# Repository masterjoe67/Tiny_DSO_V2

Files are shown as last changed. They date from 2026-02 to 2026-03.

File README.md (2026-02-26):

# Tiny_DSO_V2: 65MSPS Digital Storage Oscilloscope

Un oscilloscopio digitale ad alte prestazioni basato su architettura eterogenea **FPGA (Intel Cyclone IV)** e **Soft-Processor AVR**. Progettato per l'acquisizione di segnali in tempo reale con risoluzione a 12 bit.

<p align="center">
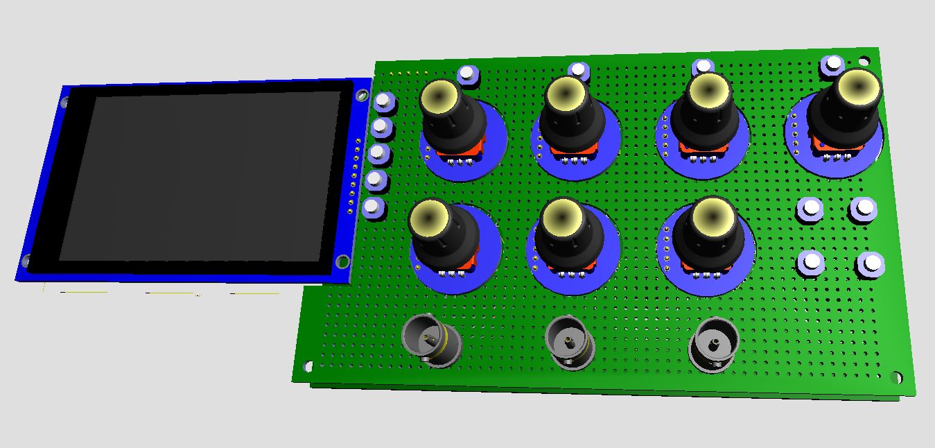
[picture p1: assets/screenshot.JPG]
Tiny DSO Preview
  
</p>

## 🚀 Caratteristiche Principali
- **Sampling Rate:** 65 MSPS (Real-time) tramite ADC parallelo.
- **Risoluzione:** 12 bit (AD9226).
- **Core CPU:** AVR V8 Soft-Core sintetizzato @ 60 MHz.
- **Trigger Engine:** Unità hardware dedicata con latenza di 15.4ns.
- **Display:** Supporto per controller ST7789 tramite SPI hardware ottimizzata.
- **Toolchain:** Compilato con l'ultima versione di AVR-GCC (15.1).

## 🛠️ Architettura del Sistema
Il progetto si divide in due componenti principali che lavorano in sinergia:

### 1. Hardware (VHDL/Verilog)
La logica programmabile gestisce le operazioni "time-critical":
- **ADC Controller:** Interfaccia parallela per l'AD9226 che cattura 12 bit per ciclo di clock.
- **Trigger System:** Monitoraggio continuo della soglia e gestione delle modalità `trigger_source`, `trigger_slope` e `trigger_mode`.
- **Memory Buffer:** Implementazione di buffer circolari in Block RAM per evitare la perdita di campioni durante la lettura della CPU.

### 2. Firmware (C)
Il software gestisce l'intelligenza dello strumento:
- **Rendering Differenziale:** Algoritmo ottimizzato per aggiornare solo i pixel necessari della traccia, riducendo il carico sul bus del display.
- **Interfaccia Utente:** Gestione degli input per la regolazione di scale temporali, offset e parametri di trigger.

## 📦 Requisiti di Sviluppo
- **FPGA:** Intel/Altera Cyclone IV (es. EP4CE22).
- **IDE:** Quartus Prime (per la sintesi hardware).
- **Toolchain:** AVR-GCC 15.1 o superiore (per il firmware).
- **Hardware ADC:** Modulo AD9226 (12-bit, 65MSPS).

---
*Developed by MJE 2026. Special thanks to M. Montanari (Perry) for the experimental PCB layout and wiring.*

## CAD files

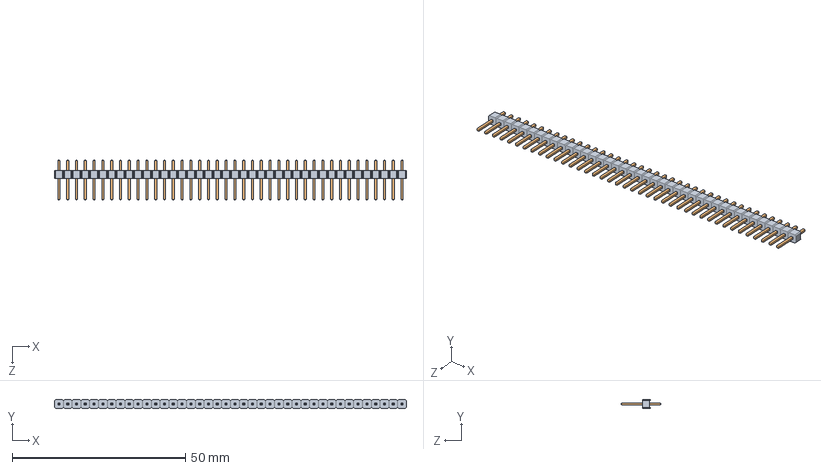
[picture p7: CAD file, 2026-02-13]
HARDWARE/CAD/User Library-Header_Male_40Pin/User Library-Header_Male_40Pin.sldasm
101.6 x 2.49 x 11.5 mm
User Library-Header_Male_40Pin_BodyArray
User Library-Header_Male_40Pin_PinArray

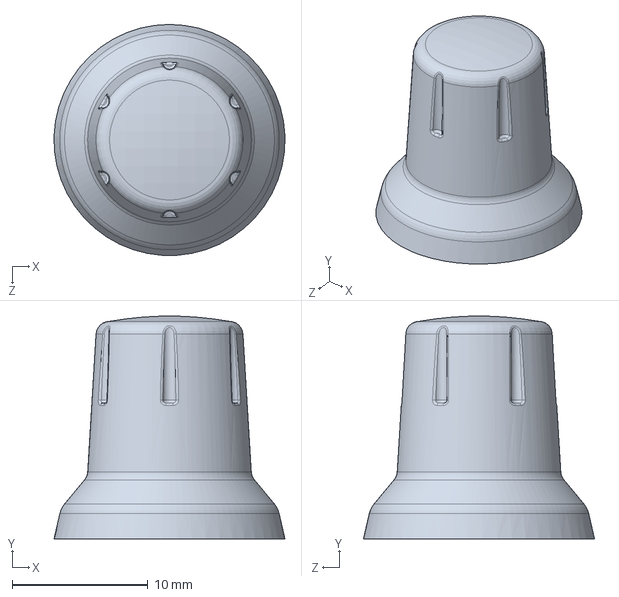
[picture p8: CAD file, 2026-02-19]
HARDWARE/CAD/Encoder/Manopola.SLDPRT
17.0 x 16.4 x 17.0 mm

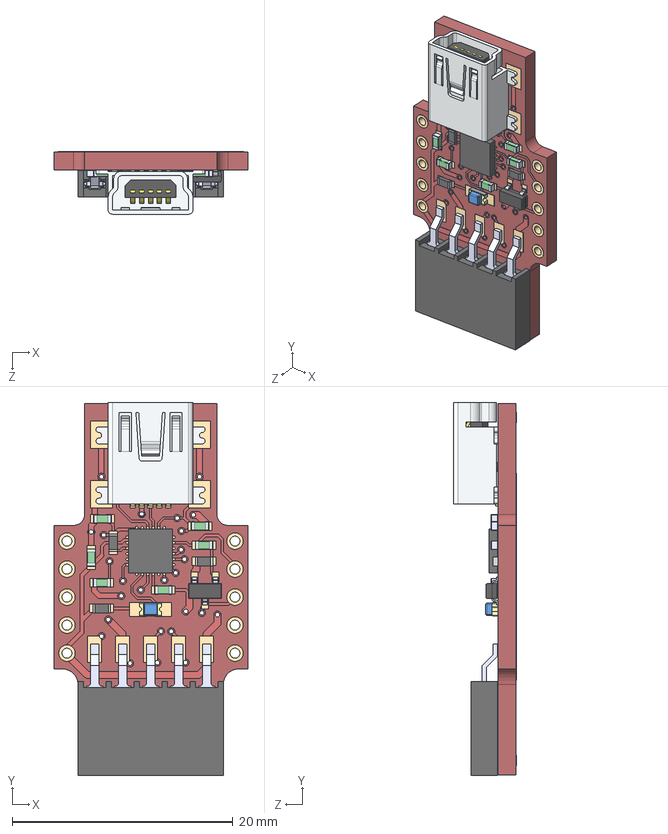
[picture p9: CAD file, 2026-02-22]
HARDWARE/CAD/uUSB-PA5-II.STEP
17.6 x 33.8 x 5.67 mm
uUSB-PA5-REV3.0aOutLine
Samtec-MUSB-05-S-B-SM-A^CN1_uUSB-PA5-REV3.0a-Components22
C-8-3_1st row (Default)^SMH-105-02-X-S_H1_uUSB-PA5-REV3.0a-Components22 x 5
ssw-xx-x_-S^SMH-105-02-X-S_H1_uUSB-PA5-REV3.0a-Components22
User Library-led_0805LED0805_blue^LED1_uUSB-PA5-REV3.0a-Components22
User Library-RES_0603L_RES_0603_Lead_1^User Library-RES_0603L x 6
User Library-RES_0603L_RES_0603_Body_1^User Library-RES_0603L x 3
User Library-cap_0603_lowprofile x 6
SW3DPS-SOT-23-DEFAULT^Q1_uUSB-PA5-REV3.0a-Components22
Extruded^9950061008_U1_uUSB-PA5-REV3.0a-Components22

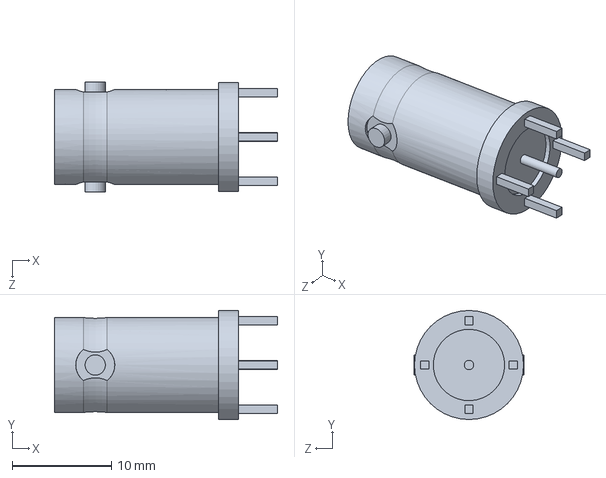
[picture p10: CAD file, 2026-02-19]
HARDWARE/CAD/BNC.SLDPRT
22.5 x 11.0 x 11.1 mm

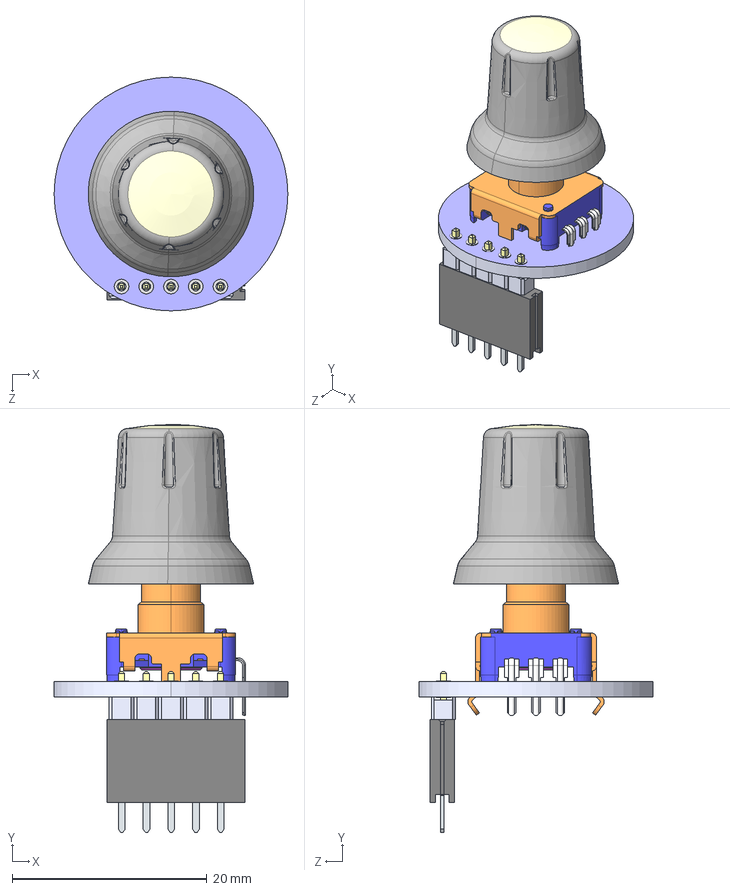
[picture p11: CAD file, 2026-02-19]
HARDWARE/CAD/Encoder/ENCODER_MODULE.STEP
24.0 x 41.9 x 24.0 mm

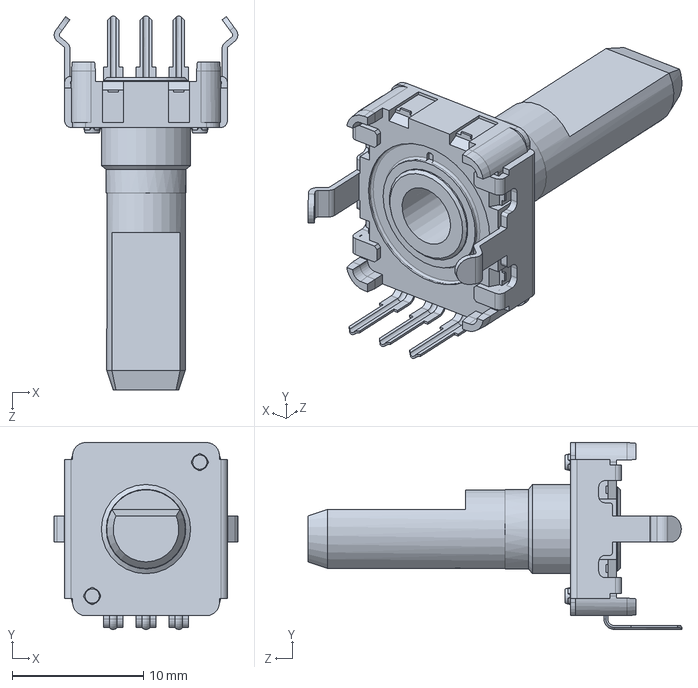
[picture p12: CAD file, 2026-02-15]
HARDWARE/CAD/Encoder/ec12e24204a9.SLDPRT
14.0 x 14.2 x 28.5 mm

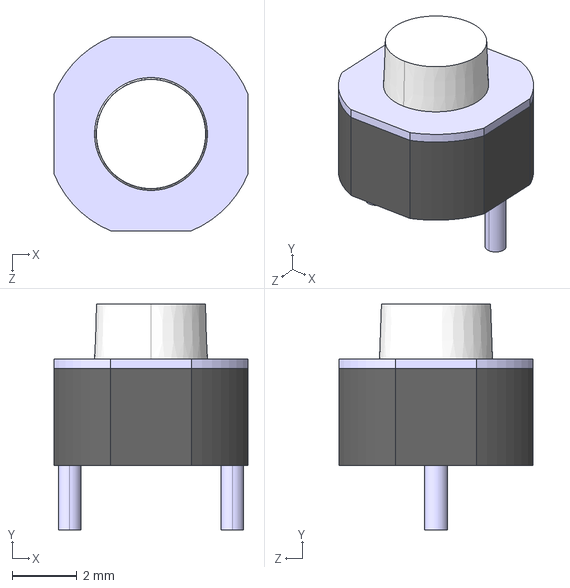
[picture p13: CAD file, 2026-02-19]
HARDWARE/CAD/Pulsante.STEP
6.00 x 7.00 x 6.00 mm

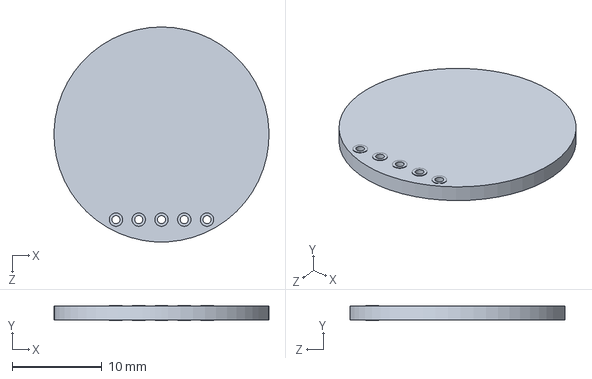
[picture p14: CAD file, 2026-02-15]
HARDWARE/CAD/Encoder/PCB_encoder.SLDPRT
24.0 x 1.70 x 24.0 mm

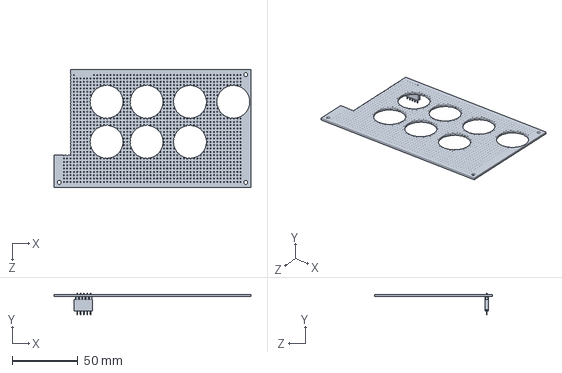
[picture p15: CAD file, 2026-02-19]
HARDWARE/CAD/Tastiera_per_step.SLDPRT
150.0 x 16.5 x 90.0 mm

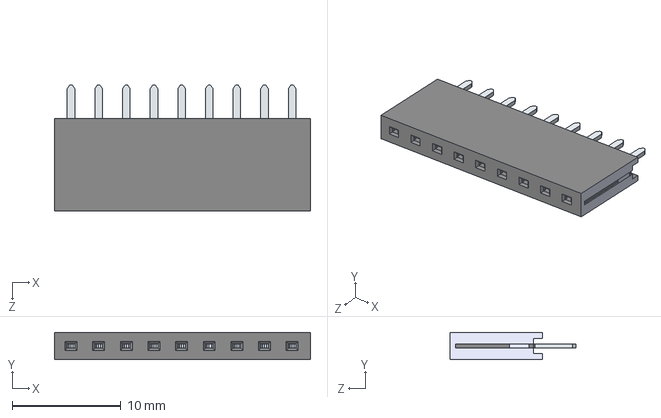
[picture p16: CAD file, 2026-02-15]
HARDWARE/CAD/Strip_9pinF.STEP
23.5 x 2.50 x 11.6 mm

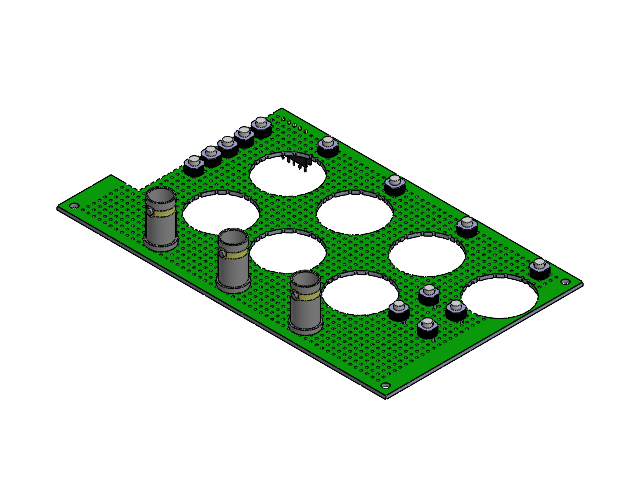
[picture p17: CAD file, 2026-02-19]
HARDWARE/CAD/Tastiera_completa.SLDASM
Tastiera_per_step
Pulsante x 13
BNC x 3

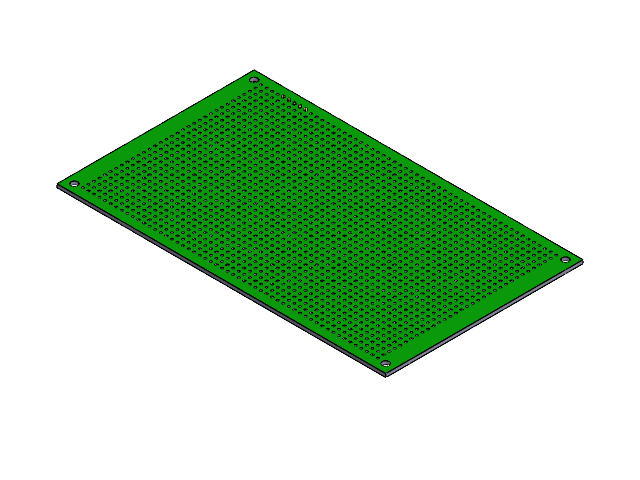
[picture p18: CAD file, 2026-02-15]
HARDWARE/CAD/Tastiera.SLDASM
Tastiera
StripBody_5pin
StripPin_5pin
Strip_5pinF

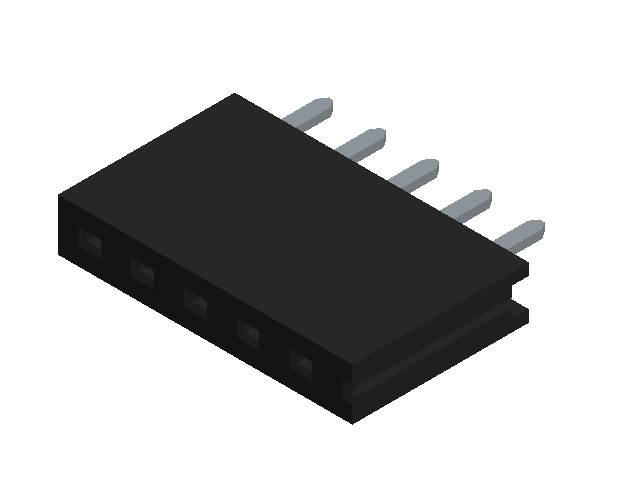
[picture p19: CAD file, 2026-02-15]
HARDWARE/CAD/Strip_5pinF.SLDASM


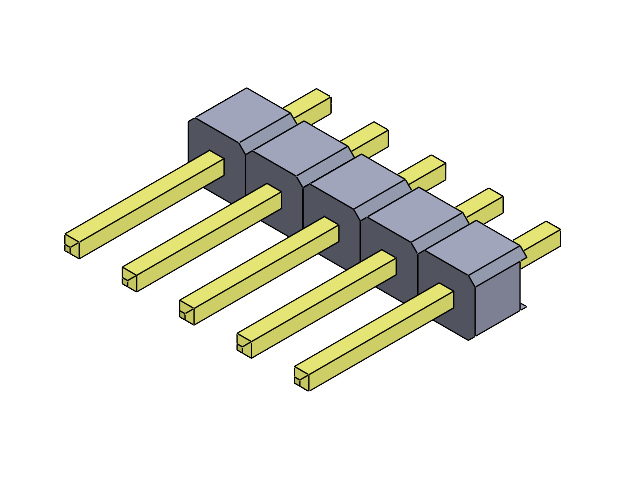
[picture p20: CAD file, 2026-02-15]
HARDWARE/CAD/Strip_5pin.SLDASM
StripBody_5pin
StripPin_5pin

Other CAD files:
HARDWARE/CAD/Strip_33pinF.SLDASM
HARDWARE/CAD/Strip_9pin.SLDASM
HARDWARE/CAD/User Library-Header_Male_40Pin/User Library-Header_Male_40Pin_PinArray.sldprt
HARDWARE/CAD/User Library-Header_Male_40Pin/User Library-Header_Male_40Pin_BodyArray.sldprt
HARDWARE/CAD/1000fori.SLDPRT
HARDWARE/CAD/178745139-7-61303211821/61303211821.SLDASM
HARDWARE/CAD/178745139-7-61303211821/61303211821_01.SLDPRT
HARDWARE/CAD/178745139-7-61303211821/61303211821_02.SLDPRT
HARDWARE/CAD/178745139-7-61303211821/61303211821_03.SLDPRT
HARDWARE/CAD/178745139-7-61303211821/61303211821_04.SLDPRT
HARDWARE/CAD/178745139-7-61303211821/61303211821_05.SLDPRT
HARDWARE/CAD/178745139-7-61303211821/61303211821_06.SLDPRT
HARDWARE/CAD/178745139-7-61303211821/61303211821_07.SLDPRT
HARDWARE/CAD/178745139-7-61303211821/61303211821_08.SLDPRT
HARDWARE/CAD/178745139-7-61303211821/61303211821_09.SLDPRT
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

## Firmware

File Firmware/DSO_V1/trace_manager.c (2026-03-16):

#include <stdbool.h>
#include <math.h>

#include "trace_manager.h"
#include "scope_shared.h"

static int16_t last_trig_y = -100; // Inizializzato fuori schermo
static Point_t old_trig_a, old_trig_b, old_trig_c;

// Creiamo dei puntatori che puntano a quella zona
uint16_t *ch1_buffer = (uint16_t *)(RAM_EXTRA_START);
uint16_t *ch2_buffer = (uint16_t *)(RAM_EXTRA_START + 800); // 800 byte dopo (400 samples * 2)

// Puntatori ai buffer "storici" (vecchi dati per cancellazione)
int16_t *old_buffer_a = (int16_t *)(RAM_EXTRA_START + 1600);
int16_t *old_buffer_b = (int16_t *)(RAM_EXTRA_START + 2400);

Point_t old_a = { 0, 0 };
Point_t old_b = { 0, 0 };
Point_t old_c = { 0, 0 };
Point_t gnd_mark_a[2] = {{ 0, 0 }, { 0, 0 }};
Point_t gnd_mark_b[2] = {{ 0, 0 }, { 0, 0 }};
Point_t gnd_mark_c[2] = {{ 0, 0 }, { 0, 0 }};

/***************************************************************************************
** Function name:           calcola_XY_coordinata
** Description:             Mappa i valori ADC per la modalità XY. 
** is_x_axis = true  -> Mappa su larghezza (Area XY)
** is_x_axis = false -> Mappa su altezza (come calcolaYTraccia)
***************************************************************************************/
int16_t calcola_XY_coordinata(Channel *ch, uint16_t valoreADC_12bit, bool is_x_axis) {
    static const float RANGE_TOTALE = 10.0f; 
    static const float ADC_RESOLUTION = 4096.0f;
    static const float BITS_PER_VOLT = ADC_RESOLUTION / RANGE_TOTALE;
    static const float ADC_ZERO = 2048.0f;
    static const float PIXEL_PER_DIV = 30.0f;

    // 1. Calcolo del delta (identico alla tua funzione)
    float deltaADC = (float)valoreADC_12bit - ADC_ZERO;
    float volt = deltaADC / BITS_PER_VOLT;
    float pixelSpostamento = (volt / ch->volts_div) * PIXEL_PER_DIV;

    if (is_x_axis) {
        // --- ASSE X (Orizzontale) ---
        // Prendiamo l'offset del canale (che Joe muove con l'encoder)
        // e lo trasliamo dall'area verticale all'area orizzontale XY.
        // Se ch->offset è 120 (centro verticale), deve diventare 325 (centro XY)
        
        int16_t offset_traslato_x = ch->offset + (205 - MARGIN_Y); 
        
        if (ch->inverted) {
            return (int16_t)(offset_traslato_x - pixelSpostamento);
        } else {
            return (int16_t)(offset_traslato_x + pixelSpostamento);
        }
    } else {
        // --- ASSE Y (Verticale) ---
        // Usiamo esattamente la tua logica originale
        if (ch->inverted) {
            return (int16_t)(ch->offset - pixelSpostamento);
        } else {
            return (int16_t)(ch->offset + pixelSpostamento);
        }
    }
}

/***************************************************************************************
** Function name:           draw_trace
** Description:             Disegna e cancella la traccia usando la logica V/div
***************************************************************************************/
void draw_dual_trace_from_bram(Channel *ch_a, Channel *ch_b, int16_t *old_buf_a, int16_t *old_buf_b, uint16_t length, bool vectors)
{
    const int16_t Y_MIN = MARGIN_Y;
    const int16_t Y_MAX = MARGIN_Y + TRACE_H - 2;

    // --- 1. RESET VARIABILI MISURE (Locali, non static!) ---
    uint64_t sum_sq = 0; 
    int64_t sum_raw_acc = 0;
    int32_t max_adc = -1;    // Inizializzazione per forzare il primo aggiornamento
    int32_t min_adc = 4096; 
    uint16_t samples_misure = 0;

    // --- 2. CALCOLO MISURE (Ciclo lineare su tutto il buffer) ---
    if(misure->active) {
        for(uint16_t m = 0; m < 400; m++) {
            // Prendiamo il dato e forziamo la pulizia a 12 bit
            uint16_t val = (misure->source == 1) ? (uint16_t)ch1_buffer[m] : (uint16_t)ch2_buffer[m];
            val &= 0x0FFF; 

            // Aggiornamento picchi: solo se il valore è nel range reale dell'ADC
            if ((int32_t)val > max_adc) max_adc = (int32_t)val;
            if ((int32_t)val < min_adc) min_adc = (int32_t)val;

            // Accumulo per Vavg (media)
            sum_raw_acc += val;

            // Accumulo per Vrms centrato su 2048
            int32_t centrato = (int32_t)val - 2048;
            sum_sq += (uint64_t)((int64_t)centrato * centrato);
            
            samples_misure++;
        }
    }

    // --- 3. LOGICA TIMING DISEGNO (Invariata) ---
    uint32_t step_fp; uint32_t ram_idx_fp;   
    if (current_time_base_idx == 0) { step_fp = (150UL << 8) / length; ram_idx_fp = 125UL << 8; } 
    else if (current_time_base_idx == 1) { step_fp = (300UL << 8) / length; ram_idx_fp = 50UL << 8; } 
    else { step_fp = 1UL << 8; ram_idx_fp = 0; }

    int16_t y_prev_new_a = -100, y_prev_old_a = -100;
    int16_t y_prev_new_b = -100, y_prev_old_b = -100;


   // --- 4. LOOP DI DISEGNO (Cancellazione SEMPRE, Tracciamento solo se ENABLED) ---
    for (uint16_t i = 0; i < length; i++) {
        uint16_t x = i + MARGIN_X;
        uint16_t ram_idx = (uint16_t)(ram_idx_fp >> 8);
        if (ram_idx >= 400) ram_idx = 399;

        // --- GESTIONE CANALE A ---
        // 1. CANCELLAZIONE (Sempre, se il vecchio punto era valido)
        if (old_buf_a[i] > Y_MIN && old_buf_a[i] < Y_MAX) {
            if (vectors && i > 0 && y_prev_old_a > Y_MIN) 
                tft_drawLine_Clipped(x-1, y_prev_old_a, x, old_buf_a[i], BLACK, Y_MIN, Y_MAX);
            else 
                tft_drawPixel(x, old_buf_a[i], BLACK);
        }
        y_prev_old_a = old_buf_a[i];

        // 2. DISEGNO NUOVO PUNTO (Solo se abilitato)
        if (ch_a->enabled) {
            int16_t y_now_a = calcolaYTraccia(ch_a, ch1_buffer[ram_idx], false);
            if (y_now_a > Y_MIN && y_now_a < Y_MAX) {
                if (vectors && i > 0 && y_prev_new_a > Y_MIN) 
                    tft_drawLine_Clipped(x-1, y_prev_new_a, x, y_now_a, ch_a->color, Y_MIN, Y_MAX);
                else 
                    tft_drawPixel(x, y_now_a, ch_a->color);
            }
            y_prev_new_a = y_now_a;
            old_buf_a[i] = y_now_a; // Salva per cancellarlo al prossimo giro
        } else {
            old_buf_a[i] = -100;    // Segna come vuoto per i prossimi cicli
            y_prev_new_a = -100;
        }

        // --- GESTIONE CANALE B ---
        // 1. CANCELLAZIONE
        if (old_buf_b[i] > Y_MIN && old_buf_b[i] < Y_MAX) {
            if (vectors && i > 0 && y_prev_old_b > Y_MIN) 
                tft_drawLine_Clipped(x-1, y_prev_old_b, x, old_buf_b[i], BLACK, Y_MIN, Y_MAX);
            else 
                tft_drawPixel(x, old_buf_b[i], BLACK);
        }
        y_prev_old_b = old_buf_b[i];

        // 2. DISEGNO NUOVO PUNTO
        if (ch_b->enabled) {
            int16_t y_now_b = calcolaYTraccia(ch_b, ch2_buffer[ram_idx], false);
            if (y_now_b > Y_MIN && y_now_b < Y_MAX) {
                if (vectors && i > 0 && y_prev_new_b > Y_MIN) 
                    tft_drawLine_Clipped(x-1, y_prev_new_b, x, y_now_b, ch_b->color, Y_MIN, Y_MAX);
                else 
                    tft_drawPixel(x, y_now_b, ch_b->color);
            }
            y_prev_new_b = y_now_b;
            old_buf_b[i] = y_now_b;
        } else {
            old_buf_b[i] = -100;
            y_prev_new_b = -100;
        }

        ram_idx_fp += step_fp;
    }

    // --- 5. CALCOLO FINALE MISURE (Senza ambiguità) ---
    if(misure->active && samples_misure > 0) {
        Channel *ch_src = (misure->source == 1) ? ch_a : ch_b;
        const float LSB = (10.0f / 4096.0f) * ch_src->multiplier;

        // Calcolo Vpp: usiamo int32_t per la differenza e poi forziamo il valore assoluto
        int32_t delta = max_adc - min_adc;
        if (delta < 0) delta = 0; // Protezione contro inizializzazioni fallite
        misure->vpp = (float)delta * LSB;

        // Vavg
        float avg_raw = ((float)sum_raw_acc / (float)samples_misure) - 2048.0f;
        misure->vavg = avg_raw * LSB;

        // Vrms
        float rms_pts = sqrtf((float)sum_sq / (float)samples_misure);
        misure->vrms = rms_pts * LSB;
    }
}


/***************************************************************************************
** Function name:           draw_xy_trace
** Description:             Rendering della traccia in modalità X-Y (Lissajous).
** Utilizza il CH1 come asse X e il CH2 come asse Y. La funzione 
** gestisce la cancellazione selettiva dei vecchi pixel tramite 
** buffer di memoria per garantire fluidità senza flickering.
** Parameters:              ch_x, ch_y: puntatori ai canali sorgente
** old_x_buf, old_y_buf: buffer storici per la cancellazione
** length: numero di campioni da processare
***************************************************************************************/
void draw_xy_trace(Channel *ch_x, Channel *ch_y, int16_t *old_x_buf, int16_t *old_y_buf, uint16_t length) 
{
    // Confini dell'area XY quadrata
    const int16_t OFFSET_X = OFFSET_XY_AREA; 
    const int16_t X_MIN = OFFSET_X;
    const int16_t X_MAX = OFFSET_X + 240;
    const int16_t Y_MIN = MARGIN_Y;
    const int16_t Y_MAX = MARGIN_Y + 240;

    for (uint16_t i = 0; i < length; i++) {
        // --- 1. CANCELLAZIONE (Usa i buffer esistenti) ---
        if (old_x_buf[i] != -100) {
            tft_drawPixel(old_x_buf[i], old_y_buf[i], BLACK);
        }

        // --- 2. CALCOLO NUOVO PUNTO ---
        if (ch_x->enabled && ch_y->enabled) {
            
            // Usiamo la TUA funzione calcolaYTraccia che funziona bene
            // Per la Y è diretta:
            int16_t raw_y = calcolaYTraccia(ch_y, ch2_buffer[i], false);
            
            // Per la X usiamo la stessa funzione, ma dobbiamo "spostarla"
            // perché calcolaYTraccia restituisce una coordinata verticale (Y).
            // Noi sottraiamo il suo margine verticale e aggiungiamo quello orizzontale XY.
            int16_t raw_x = calcolaYTraccia(ch_x, ch1_buffer[i], false);
            int16_t new_x = raw_x - MARGIN_Y + OFFSET_X;
            int16_t new_y = raw_y;

            // --- 3. DISEGNO E SALVATAGGIO ---
            // Verifichiamo che il punto sia dentro il quadrato 240x240
            if (new_x >= X_MIN && new_x < X_MAX && new_y >= Y_MIN && new_y < Y_MAX) {
                tft_drawPixel(new_x, new_y, GREEN);
                old_x_buf[i] = new_x;
                old_y_buf[i] = new_y;
            } else {
                old_x_buf[i] = -100; // Segnaposto fuori schermo
            }
        }
    }
}

/***************************************************************************************
** Function name:           calcolaYTraccia
** Description:             Converte il valore ADC in coordinata Y pixel basandosi
** sui parametri del canale (V/div, offset, invert).
***************************************************************************************/
int16_t calcolaYTraccia(Channel *ch, uint16_t valoreADC_12bit, bool isTrigger) {
    static const float RANGE_TOTALE = 10.0f; 
    static const float ADC_RESOLUTION = 4096.0f;
    static const float BITS_PER_VOLT = ADC_RESOLUTION / RANGE_TOTALE; // 409.6
    static const float ADC_ZERO = 2048.0f;
    static const float PIXEL_PER_DIV = 30.0f;

    // 1. Delta rispetto al centro
    float deltaADC = (float)valoreADC_12bit - ADC_ZERO;

    // 2. Volt reali
    float volt = deltaADC / BITS_PER_VOLT;

    // 3. Quanti pixel si deve spostare (es. 1V = 2 divisioni = 60 pixel)
    float pixelSpostamento = (volt / ch->volts_div) * PIXEL_PER_DIV;

    // --- CORREZIONE INVERSIONE ---
    // Se il segnale è positivo (volt > 0), vogliamo che la Y diminuisca 
    // per andare verso l'alto dello schermo.
    if (ch->inverted) {
        return (int16_t)(ch->offset - pixelSpostamento); 
    } else {
        return (int16_t)(ch->offset + pixelSpostamento);
    }
}
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

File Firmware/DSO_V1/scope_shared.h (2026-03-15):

#ifndef SCOPE_SHARED_H
#define SCOPE_SHARED_H

#include <stdint.h>
#include <stdbool.h>
#include "Peripheral/st7798.h"

#define F_SYS_CLK 60000000UL
#define REG_INDEX   _SFR_IO8(0x3C) //(*(volatile uint8_t*)0x81)
#define REG_CHA     _SFR_IO8(0x13)
#define REG_CHB     _SFR_IO8(0x14)
#define TRIG_CTRL_REG     _SFR_IO8(0x15)
#define REG_TRIG    _SFR_IO8(0x35)
#define REG_FREQ0     _SFR_IO8(0x00)
#define REG_FREQ1     _SFR_IO8(0x01)
#define REG_FREQ2     _SFR_IO8(0x02)
#define REG_FREQ3     _SFR_IO8(0x03)
#define INDEX_RESET   _SFR_IO8(0x1C)
#define REG_BASETIME        _SFR_IO8(0x14)
#define REG_TRIGGER_LEVEL   _SFR_IO8(0x13)
#define REG_TRIGGER_MODE    _SFR_IO8(0x15)

#define BRAM_START_ADDR 0x4000
#define BRAM_DATA_PTR   ((volatile uint8_t *)0x4000)

// Definiamo l'inizio della RAM "extra" (dopo i primi 4KB dell'ATmega128)
// L'indirizzo 0x1100 è l'inizio della zona oltre i 4KB standard
#define RAM_EXTRA_START 0x1100
#define ADDR_OLD_A (int16_t*)(0x1740)
#define ADDR_OLD_B (int16_t*)(0x1A60)

// Indirizzi base del Co-Processore
// --- CONFIGURAZIONE CANALE 1 ---
#define REG_CH1_SCALE_L   0x4010  // Scrittura: Scala bit 7-0
#define REG_CH1_SCALE_H   0x4011  // Scrittura: Scala bit 15-8
#define REG_CH1_OFFSET_L  0x4012  // Scrittura: Offset bit 7-0
#define REG_CH1_OFFSET_H  0x4013  // Scrittura: Offset bit 15-8

// --- CONFIGURAZIONE CANALE 2 ---
#define REG_CH2_SCALE_L   0x4014  // Scrittura: Scala bit 7-0
#define REG_CH2_SCALE_H   0x4015  // Scrittura: Scala bit 15-8
#define REG_CH2_OFFSET_L  0x4016  // Scrittura: Offset bit 7-0
#define REG_CH2_OFFSET_H  0x4017  // Scrittura: Offset bit 15-8

// --- INPUT ADC E TRIGGER CALCOLO ---
#define REG_CH1_ADC_L     0x4018  // Scrittura: Byte basso ADC (Parcheggio)
#define REG_CH1_ADC_H     0x4019  // Scrittura: Byte alto ADC (Trigger Calcolo CH1)
#define REG_CH2_ADC_L     0x401A  // Scrittura: Byte basso ADC (Parcheggio)
#define REG_CH2_ADC_H     0x401B  // Scrittura: Byte alto ADC (Trigger Calcolo CH2)

// --- RISULTATO CALCOLO (LETTURA) ---
#define REG_Y_RESULT_L    0x401C  // Lettura: y_result bit 7-0
#define REG_Y_RESULT_H    0x401D  // Lettura: y_result bit 15-8

#define REG_TRIG_HYST    0x401E  // Scrittura: Trigger Hysteresis (0-255, in LSB)

#define REG_DDS_ADDR 0x401F  // Frequenza di uscita del DDS (4 byte, 32 bit unsigned int)

#define XRAM_WRITE(addr, val) (*(volatile uint8_t *)(addr) = (val))
#define XRAM_READ(addr) (*(volatile uint8_t *)(addr))

#define TRIG_CTRL_BIT  7         // il bit che sblocca wr_ptr

#define PRE_TRIGGER       200
#define POST_TRIGGER      200
#define BUFFER_TOTAL      (PRE_TRIGGER + POST_TRIGGER)
#define READY_BIT         1
#define BUFFER_SIZE       4096
#define DISPLAY_SAMPLES   255
#define PAN_LIMIT         200   
#define PAN_STEP          4

#define TRACE_W 400
#define TRACE_H 240
#define MARGIN_X 5
#define MARGIN_Y 25
#define SIDEBAR_X (MARGIN_X + TRACE_W + 5)
#define CENTER_TRACE_X (MARGIN_X + (TRACE_W / 2))
#define OFFSET_XY_AREA 85

#define COUPL_DC  0
#define COUPL_AC  1
#define COUPL_GND 2

#define FREQ_AVG_SAMPLES 32

#define MENU_NONE       0
#define MENU_CH1        1
#define MENU_CH2        2
#define MENU_TRIG       3
#define MENU_MEAS       4
#define MENU_PAN        5
#define MENU_CURSORS    6
#define MENU_ORIZZONTAL 7
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

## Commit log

2026-02-06 Sostituito display con ST7798S
    [stp2.csv, stp2.stp]
2026-02-07 Debug vari
    [stp2.stp]
2026-02-08 Implementazione misura di frequenza
    [stp2.stp]
2026-02-10 fix: risolto problema traccia aliena nel PAN orizzontale. Ottimizzata la logica del buffer circolare per un PAN più ampio e stabile.
2026-02-10 fix: risolto problema traccia congelata alla disattivazione canale
    La funzione draw_trace ora cancella sempre i vecchi pixel prima di verificare se il canale è abilitato al disegno.
    [stp2.csv, stp2.stp]
2026-02-10 feat: aggiunta modalità di disegno vettoriale (linee/punti)
    Implementata la logica di disegno e cancellazione per vettori e punti singoli, con gestione dinamica tramite parametro.
2026-02-13 fix: stabilità core 60MHz, ripristino Pan in STOP e correzione frequenzimetro
    FPGA (VHDL):
    - Sostituite 'variable' con 'signal' per migliorare il timing a 60MHz.
    - Corretto errore frequenza (450Hz -> 300Hz) con registro trig_prev_val.
    - Arming con isteresi sincronizzato.
    AVR (C):
    - Disegno svincolato dallo stato RUN (refresh continuo).
    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
    [ST7789S.SLDPRT, ST7789SModule.SLDASM, ST7789SModule.SLDPRT, ST7789SModule.STEP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]
2026-02-15 fix(fpga): rimappate alcune uscite per ottimizzazione PCB, aumentata la frequenza della porta TFT_SPI a 40MHz
    [1000fori.SLDPRT, 61303211821.SLDASM, 61303211821_01.SLDPRT, 61303211821_02.SLDPRT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]
2026-02-18 feat: migliorata stabilità encoder e aggiunti tasti ENC_KEY
    - Encoder: aumentato timer debounce a 19-bit per eliminare doppi scatti.
    - Keypad: aggiunti 4 tasti encoder (codici 15-18) con polarità fissa via generic.
    - Keypad: unificata logica di debounce e sblocco eventi per matrice e tasti diretti.
    [stp1.stp]
2026-02-18 feat: implementazione lettura encoder su AVR e fix effetto ping-pong
    - Firmware: aggiunta routine di lettura sincronizzata HI/LO per registri a 16-bit.
    - VHDL: ottimizzato sampler_timer a 18-bit (~4.3ms) per bilanciare debounce e velocità di rotazione.
    - Fix: risolto effetto ping-pong durante rotazioni rapide tramite ricalibrazione della frequenza di campionamento.
    - Firmware: mappatura delle variabili locali per i 7 canali encoder.
2026-02-19 feat: aggiunto controllo PWM backlight al controller ST7796
    - VHDL: implementato generatore PWM a 8-bit (195kHz) per il controllo luminosità.
    - MMIO: aggiunto registro LCD_PWM_REG per la gestione dinamica del backlight da CPU.
    - RTL: aggiornata interfaccia bus per supportare la lettura/scrittura del nuovo registro.
    - Hardware: aggiunta porta tft_backlight per il pilotaggio diretto del driver LED.
    [BNC.SLDPRT, ENCODER_MODULE.SLDASM, ENCODER_MODULE.SLDPRT, ENCODER_MODULE.STEP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]
2026-02-21 feat: integrazione completa controllo hardware (Encoder, Tastiera, Backlight)
    - Encoder: ottimizzato debounce a 18-bit e risolto effetto ping-pong.
    - Tastiera: estesa a 19 ingressi con integrazione 4 tasti encoder (codici 15-18).
    - TFT: aggiunto controllo PWM backlight a 8-bit (195kHz) con registro dedicato.
    - Firmware: implementata routine di lettura atomica 16-bit per registri encoder.
    - Hardware: predisposta configurazione Weak Pull-Up per ingressi digitali.
    [stp1.stp]
2026-02-21 docs: creazione README.md iniziale con specifiche hardware
    [stp1.stp]
2026-02-22 init: aggiunta logica di lettura parallela per doppio AD9226
    [uUSB-PA5-II.STEP]
2026-02-23 Pulizia del codice e remap di alcune porte
2026-02-24 build: upgrade toolchain a GCC 15.1 e fix critici
    - Corretti tipi di puntatori per ADC 12-bit (uint16_t*)
    - Risolto bug di precedenza operatori nel trigger (logica &&)
    - Aggiornato Makefile per compatibilità con avr-size moderno
    - Sistemate definizioni multiple variabili globali (extern)
2026-02-25 feat: ottimizzazione gestione tastiera e remapping I/O
    - Aggiornata la matrice di scansione dei tasti per nuovo layout
    - Rimappati i pin di input/output nel firmware per coerenza con l'hardware
    - Ottimizzata la routine di debounce per una risposta più rapida
    - Aggiornate le definizioni dei registri I/O nel file Peripheral/input.c
2026-02-27 feat(gfx): implementazione scala verticale fisica e sincronizzazione trigger
    - Rifattorizzata la funzione calcolaYTraccia con logica V/div e griglia 30px.
    - Calibrato lo zero ADC a 128 per campionamento a 8 bit.
    - Aggiunto supporto per modalità Coarse (1-2-5) e Fine (variazione continua) per gli encoder.
    - Sincronizzati i marker GND e la linea del trigger con l'offset del canale.
    - Gestione dinamica della sorgente trigger tramite puntatori e trigger_source.
    - Risolto l'effetto fisarmonica ancorando la traccia al riferimento GND.
2026-02-28 Fix: sync BRAM a 4-byte (60MHz), puntatore trigger e cleanup warning signedness
    [stp1.stp]
2026-03-01 feat(measures): refactor calcolo volt e frequenza
    Sintesi modifiche:
    1. Ottimizzazione calcolo: integrata ricerca min/max, sum_raw e sum_sq
    direttamente nel loop 'draw_dual_trace_from_bram' per ridurre accessi XRAM.
    2. Fix Precisione: convertite variabili Vpp, Vavg, Vrms da uint16_t a float
    nella struct 'Measure' per supportare i decimali.
    3. Calibrazione Hardware: implementato calcolo voltaggio basato su LSB_VOLT
    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
2026-03-02 feat: Aggiunta isteresi variabile trigger (0x401E) e ottimizzazione MMIO. Encoder a doppia funzione (Level/Hyst). Firmware rock-solid a soli 23KB. Buonanotte, Zoe.
    [stp1.stp]
2026-03-07 feat(analog-chain): ottimizzazione pipeline ADC e sincronizzazione clock a 65MHz
    SINTESI DEI CAMBIAMENTI:
    - Implementato supporto completo per clock di sistema a 65MHz (periodo campionamento 15.38ns).
    - Allineamento nomenclatura registri MMIO: -> , -> , -> .
    - Ottimizzato driver di lettura ADC: sincronizzazione dei segnali ACK/BCK per eliminare jitter in fase di acquisizione.
    - Perfezionata logica Buffer Circolare: gestione automatica dello stato di HOLD al trigger o timeout (modalità AUTO).
    - Migliorata interfaccia di lettura MCU: incremento automatico dell'indice RAM () su ciclo di lettura AVR per massimizzare il throughput.
    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
2026-03-08 feat: calibrazione sistema e ottimizzazione trigger/freq
    Dettagli modifiche:
    1. Hardware & Misure:
    - Corretta Vref da 3.3V a 5.0V reale (correzione errore lettura 0.6V -> 1V).
    - Allineamento calcolo LSB (5.0/4096) per Vpp, Vavg e Vrms.
    - Sincronizzazione grafica a 30px/div su tutte le 10 portate (10mV-10V).
    2. Trigger Dinamico:
    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
2026-03-10 Implementazione embrionale Autoset: aggiunta logica di scansione verticale e timing.
    - Introdotta routine 'configura_verticale_smart' con calcolo matematico della scala V/div (guadagno fisso +-5V).
    - Ottimizzata gestione della BRAM: ora la cattura è sincronizzata con il READY_BIT dell'FPGA.
    - Implementata funzione 'cerca_indice_timebase' con margine di sicurezza per visualizzare almeno 2-5 cicli.
    - Integrato auto-centramento del trigger level basato sui valori v_max e v_min reali.
    - Corretto bug del ghosting tracce tramite pulizia selettiva dei buffer nel loop di disegno.
2026-03-15 feat: implementata modalità X-Y (Lissajous) e menu Horizontal
    Dettagli tecnici dell'aggiornamento:
    - Implementato motore di rendering XY con mappatura asse X su CH1 e asse Y su CH2.
    - Introdotto 'set_display_mode' per la gestione pulita delle transizioni YT/XY.
    - Aggiunto reset selettivo dei buffer (old_buf_a/b) per eliminare il flickering.
    - Nuova griglia quadrata 240x240 con croce centrale e divisioni proporzionali.
    - Menu Horizontal a scomparsa con toggle per XY Mode e formato traccia (Vettori/Punti).
    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
2026-03-16 Ottimizzazione clock ADC e pulizia formattazione UI
    - Implementato ALTDDIO_OUT nel Top Level VHDL per ridurre il jitter.
    - Separati i segnali di clock per i canali ADC A e B.
    - Corretta logica di arrotondamento e soglie unità (u, m, k, M) in C.
    - Aggiunta intestazione M.J.E. ai sorgenti VHDL del Soft Core.
    [stp1.stp]
2026-03-17 Aggiornamento hardware e refactoring FPGA
    - Aggiornato schema elettrico (interfaccia ADC e clock).
    - Pulizia generale del codice VHDL del Soft Core.
    - Ottimizzati i tempi di simulazione e timescale.
    [stp1.stp]
